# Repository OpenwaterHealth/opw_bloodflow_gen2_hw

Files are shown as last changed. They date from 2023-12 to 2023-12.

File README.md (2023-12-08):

# opw_bloodflow_gen2_hw
Openwater Blood Flow Gen 2 Hardware

system

Openwater Gen 2 Blood Flow System hardware designs are detailed in this repository. 

## Table of Contents

- [Getting Started](#getting-started)
  - [Prerequisites](#prerequisites)
- [Usage](#usage)
- [Contributing](#contributing)
- [License](#license)

## Getting Started

Before getting started with the design data included in this repo, you may want to visit the Gen 2 Blood Flow Hardware Wiki for some background information on the system and its design. You may also want to review the See the [Openwater Blood Flow Gen 2 Software](link) and [Openwater Blood Flow Gen 2 Analysis](link) repos for additional information about the system and its operation. 

### Prerequisites

Required software will depend on the type of data desired by the user. In general, we have tried to include generic formats, viewable with free tools, wherever possible. Data in proprietary formats such as SolidWorks and Altium native are provided for the convenience of users with access to those tools.  

Several file types commonly used include
- STEP assembly files and SolidWorks native files for mechanical assemblies
- PDFs of assembly and component drawings, electrical schematics, datasheets, and documentation
- Gerber files for printed circuit designs
- Altium design files for circuit designs and layouts
- DXF and STL files for individual mechanical components

### Repository Contents
[Mechanical design files](mechanical), which include
- [Major subsystems](mechanical/major_subsystems)
- Additional design files for various components and subassemblies in various formats ([PDF](mechanical/pdf), [STL](mechanical/stl), [DXF](mechanical/dxf))

[Electrical design files](electrical), which includes printed circuit board assemblies and harnessing

[System design](system_design) files which include high-level documents describing the design of the blood flow system

[Assembly and Test](assembly_and_test) which includes various documents detailing contruction of various device subsystems

## Contributing

We welcome contributions from the community. If you have ideas for improvements or find any issues, please open an issue or submit a pull request.

Before contributing, please read our [Contributing Guidelines](CONTRIBUTING.md).

## License
opw_bloodflow_gen2_hw is licensed under the GNU Affero General Public License v3.0. See [LICENSE](LICENSE) for details.

## Investigational Use Only
CAUTION - Investigational device. Limited by Federal (or United States) law to investigational use. opw_bloodflow_gen2_hw has *not* been evaluated by the FDA and is not designed for the treatment or diagnosis of any disease. It is provided AS-IS, with no warranties. User assumes all liability and responsibility for identifying and mitigating risks associated with using this software.

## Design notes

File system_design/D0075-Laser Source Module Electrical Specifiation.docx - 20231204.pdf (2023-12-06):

Subsystem Specification | Doc #: | D0075
Laser Source Module Electrical Specification | Rev: | 01
| Page: | Page 1 of 10

### 1. PURPOSE

The purpose of this document is to provide specifications and relevant technical details for the laser source electrical subsystem.

### 2. SCOPE

This document provides an overview of the complete Gen 2 measurement system, Laser source module subsystem functional blocks and signal interconnect, critical component information, diode laser driver requirements and signaling, Tapered amplifier driver requirements and signaling laser safety and support components.

### 3. GOVERNING SAFETY STANDARDS AND COMPONENT REFERENCES

Document No. Document Title

All references to specific policies, procedures, or work instructions in this document are to the latest revision of that document unless otherwise noted. All references to personnel in this document are to that person or his/her designated representative unless otherwise stated.

### 4. DEFINITIONS AND ACRONYMS

### 4.1. Acronyms used in this Document

ASSY – Assembly
BOM – Bill of Materials
DWG – Drawing
FAB – Fabrication
OTS – Off the Shelf
PCA – Printed Circuit Assembly
PCB – Printed Circuit Board

### 5. GENERATION 2 LASER MEASUREMENT SYSTEM

5.1. System Overview – Measurement system is divided into seven sybsystems:
- Laser Source Module
- RVP-‐TDA4Vx Instrument Controller
- Isolation Interface Module
- Patient-‐Applied-‐Part
- Power Distribution/Regulator Module
- Trigger/Timing Module
- Laser Distribution and Control

Figure 5.1 illustrates the overall system architecture with relevant signals and interconnects shown, color coded by function.

Subsystem Specification | Doc #:

Laser Source Module Electrical Specification
Page: | Page 2 of 10

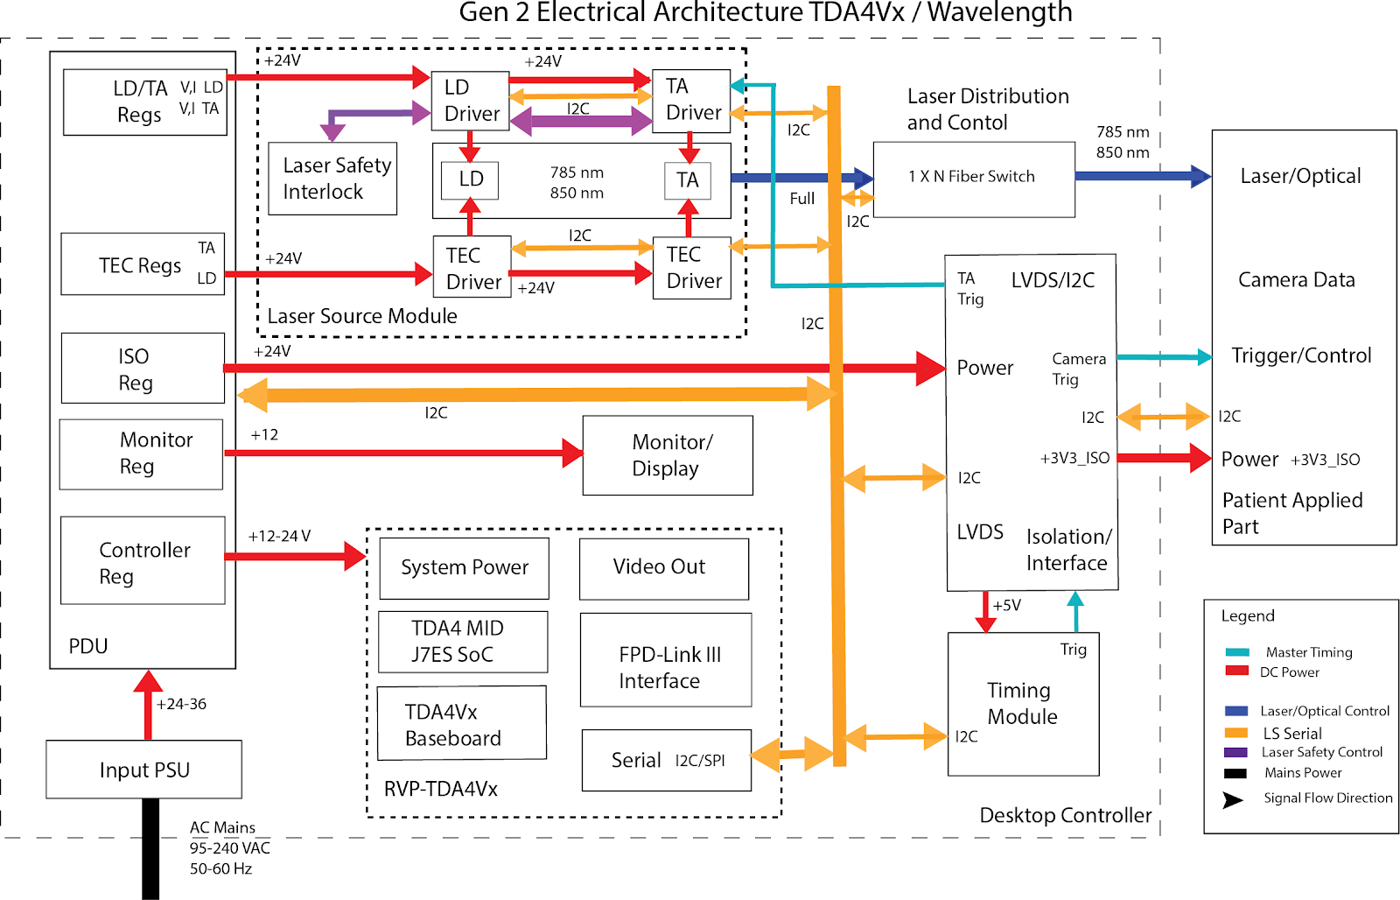
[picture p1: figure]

Figure 5.1 System Architecture

Laser Source Module-‐ Optical system used to deliver optical energy to patient. Contains two OTS semiconductor laser devices, detailed in the critical components section of this document.

RVP-‐TDA4Vx Instrument Controller-‐ Computational platform used for system control, signal and data processing and patient applied part interface.

Isolation/Interface Module-‐ | Patient-‐applied-‐part power, interface and control
Patient-‐Applied-‐Part-‐ | Device containing multiple camera sensors, control electronics, laser
distribution optics and data pathway electronics

Power Distribution/Regulator Module-‐Instrument subsystem power distribution, monitoring and control

Trigger/Timing Module-‐Instrument system master timing module. Provides timing and synchronization signals to laser source, patient applied part and instrument controller

Laser Source Module Electrical Specification
Page: | Page 3 of 10
Laser Distribution and Control-‐ | Commercial, serially controlled 1 x 8 Fiber optic switch
5.2. Laser Source Module Subsystem Detail – Diode Laser and Tapered Amplifier devices are both driven by low noise, voltage controlled current sources. Input power to these devices is supplied by discrete, individually regulated supplies from the power distribution unit. In addition to device drivers, this subsystem also provides TEC drivers for each semiconductor laser to ensure that the device operates at a constant, well defined temperature. Figure 5.2 illustrates the device driver arrangement and relationship to the power distribution unit.

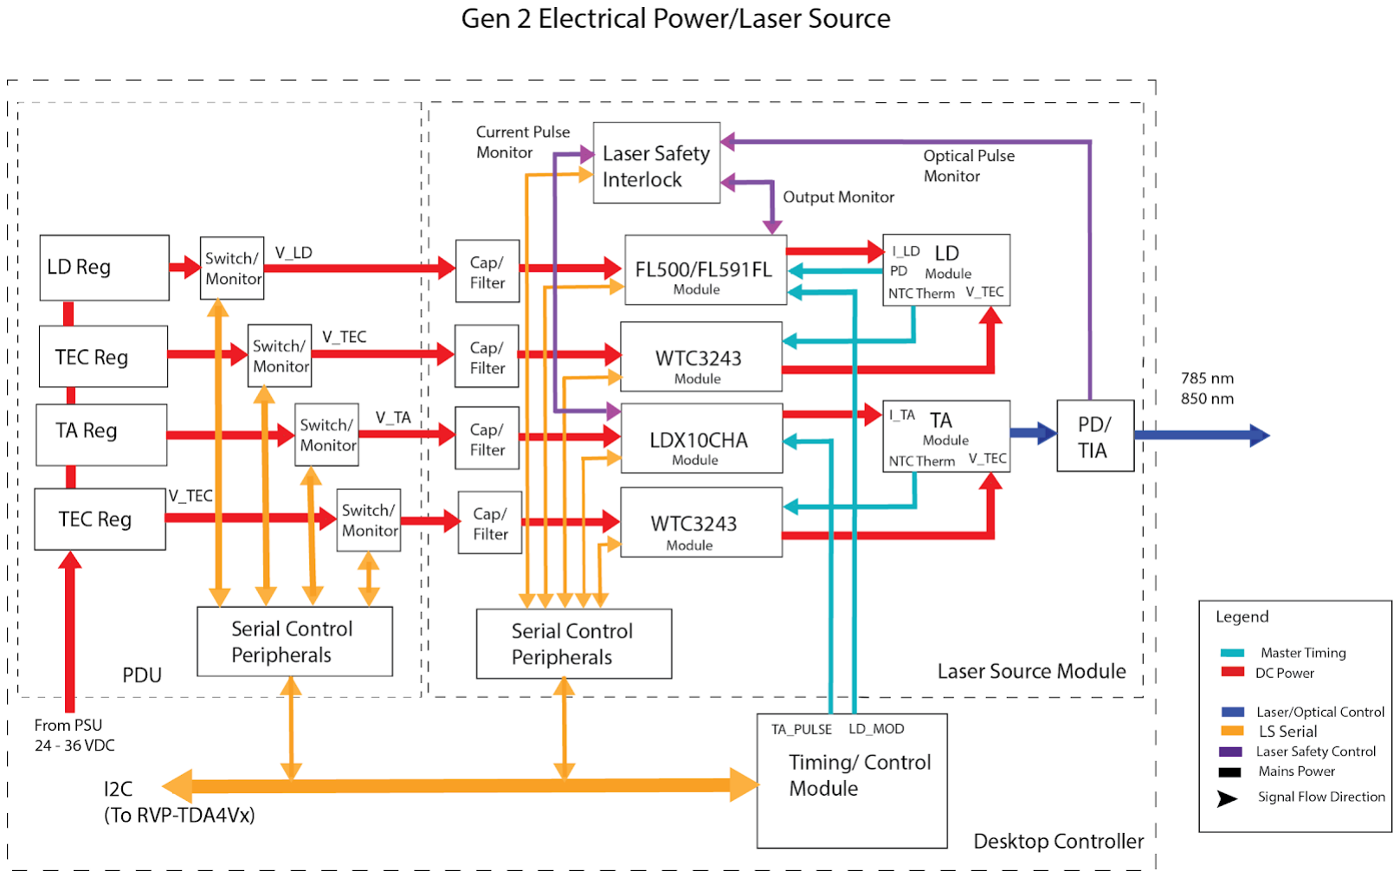
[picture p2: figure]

Figure 5.2 Laser Driver Subsystem

Architecture provides a switched, monitored low noise power supply to each of the driver modules shown in this system. Also included in this is a set of monitor and control peripherals, connected to one of the I2C networks in the system serial control backbone. Also illustrated in this diagram is the trigger/timing signals supplied to each device. Section 5.3 describes the laser diode driver in detail, and section 5.4 describes the tapered amplifier system in detail.

Laser Source Module Electrical Specification
Page: | Page 4 of 10
5.3. Laser Diode Driver – Laser diode module is a commercially sourced, single frequency diode laser module in a dual, inline butterfly type package. Figure 5.3 illustrates the device and critical specifications.

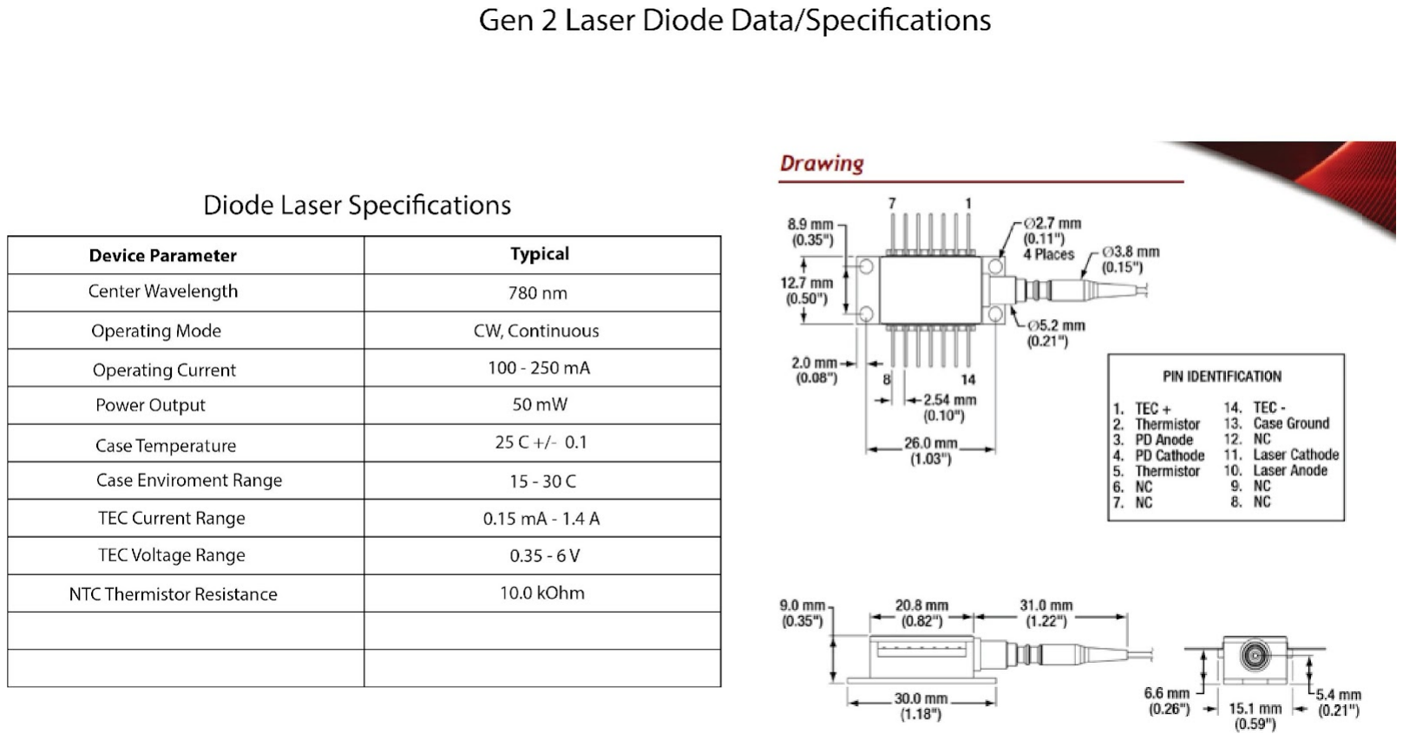
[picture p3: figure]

Figure 5.3 Laser Diode Specification

Items to note: Device is operated CW, fiber coupled, and has an integrated TEC, and NTC thermistor for temperature control. Active device is isolated from the case and the current intention is to attach the case to a defined ground potential, consistent with safety and EMC testing requirements. Temperature regulation is 25 C +/-‐ 0.1.

The diode laser driver contains a constant current driver, control and monitor electronics and is implemented using a set of commercial OTS components from Wavelength Electronics. Figure 5.4 illustrates the driver architecture and relevant Wavelength components. Note that the driver should provide support for a small signal modulation input, in addition to the CW current level. Back facet device monitor is not used in driver operation, but is used in conjunction with the Laser Safety Interlock.

Laser Source Module Electrical Specification
Page: | Page 5 of 10

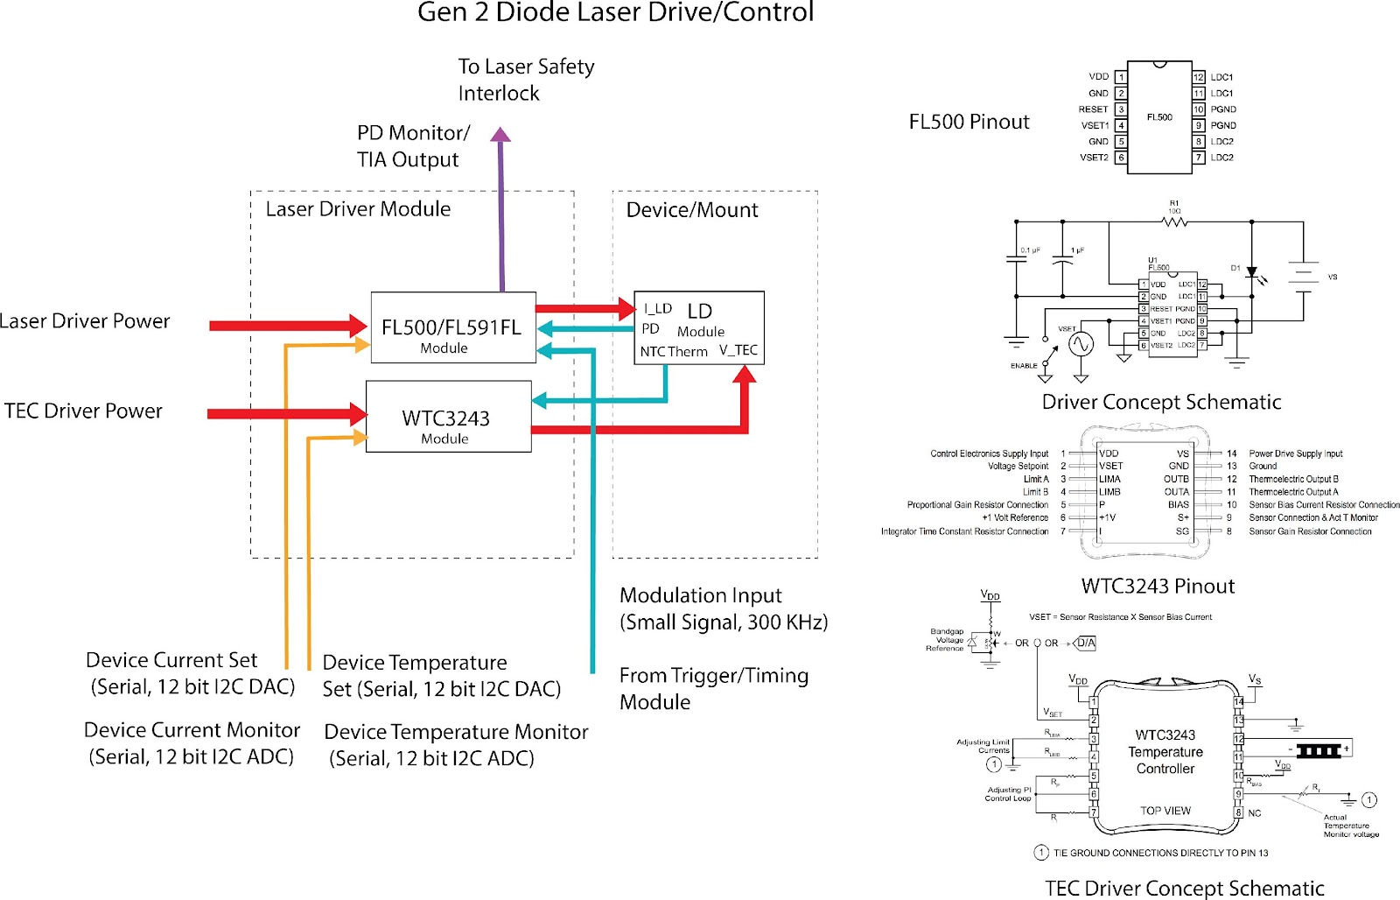
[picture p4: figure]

Figure 5.4 Laser Driver Module Details

Laser Source Module Electrical Specification
Page: | Page 6 of 10
5.4. Tapered Amplifier Driver-‐ | Tapered Amplifier module is a commercially sourced, narrow bandwidth
semiconductor laser module in a dual, inline butterfly type package. Figure 5.5 illustrates the device and critical specifications. Items to note: Device is operated QCW mode, fiber coupled, and has an integrated TEC, and NTC thermistor for temperature control. Active device is isolated from the case and the current intention is to attach the case to a defined ground potential, consistent with safety and EMC testing requirements. Temperature regulation is 25 C +/-‐ 0.1.

The Tapered Amplifier driver control and monitor electronics and is implemented using a set of commercial OTS components from Wavelength Electronics. Figure 5.6 illustrates the driver architecture and relevant Wavelength components. Note that the driver should provide support for CW operation at a lower current level than specified in the QCW peak specification

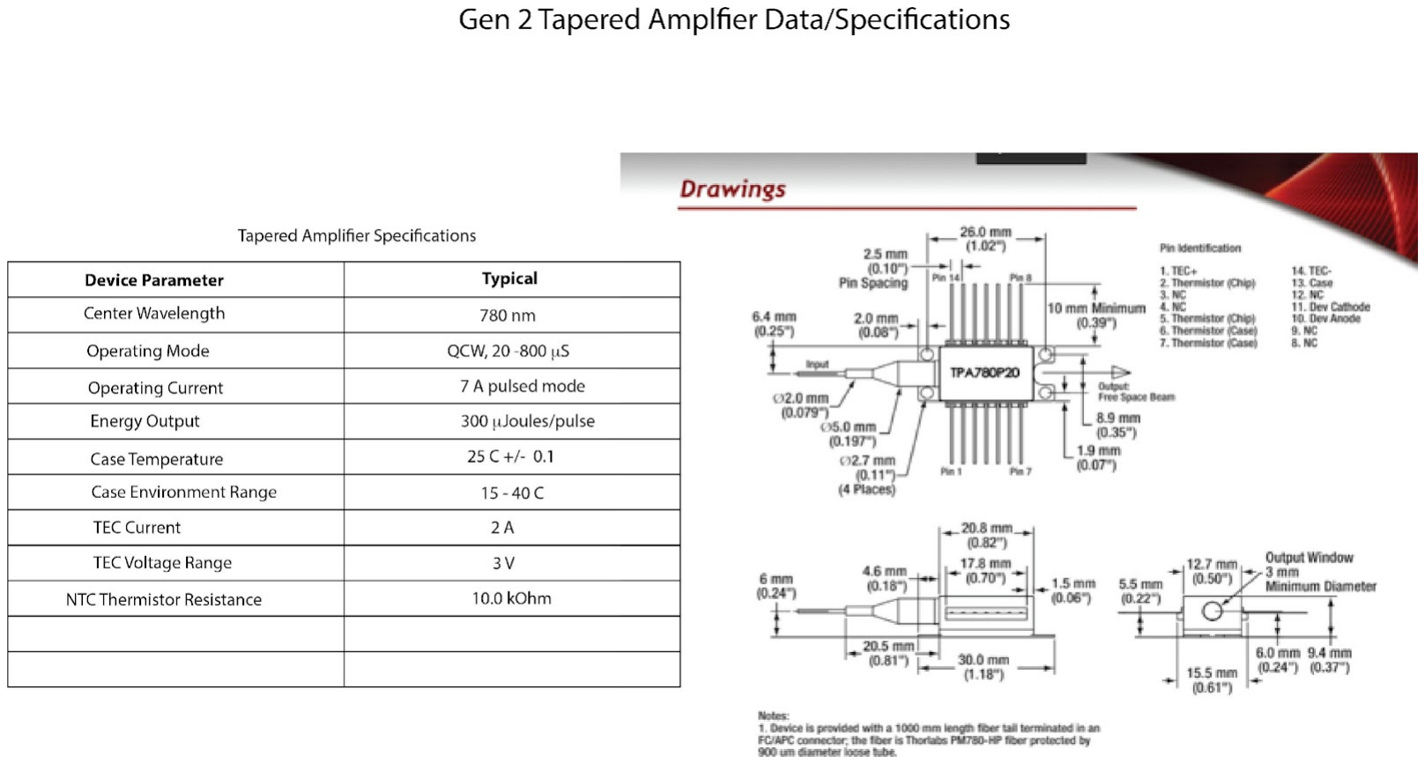
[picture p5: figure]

Laser Source Module Electrical Specification
Page: | Page 7 of 10

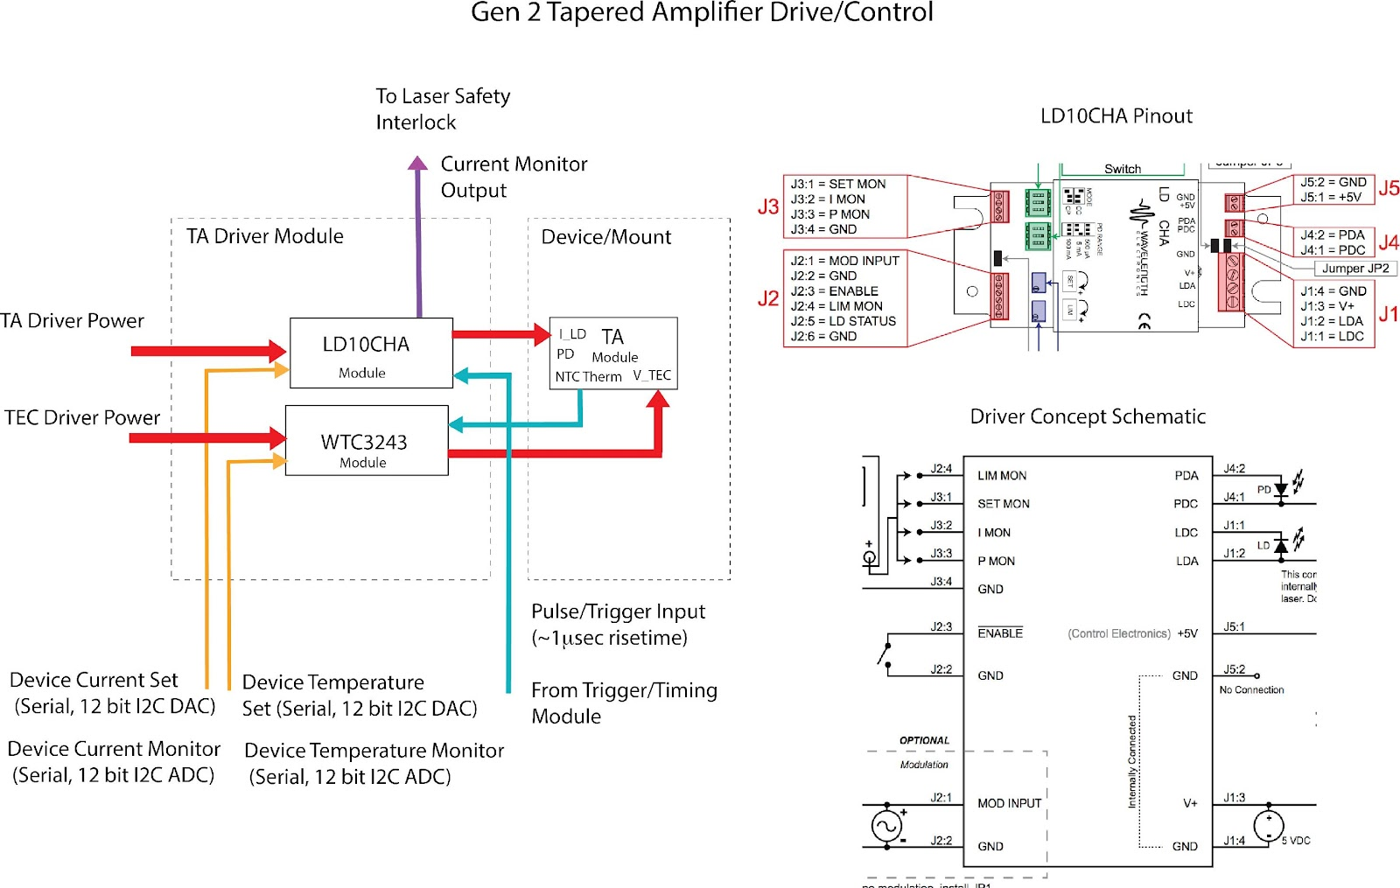
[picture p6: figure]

Figure 5.6 Tapered Amplifier Details

5.5. Laser Safety Interlock – Laser source operation uses an interlock circuit that monitors the laser for proper operation. Circuit monitors both single pulse energy and multiple pulse energy. Both electrical
and optical monitors are employed for measurements and serve to provide redundant monitoring, consistent with IEC 60825.

In addition to laser output monitoring, the interlock system also provides protection against device failure. An essential part of the monitoring system checks for Diode Laser input and proper operation of the device. Operating the Tapered Amplifier without a Diode Laser (Seed) input will lead to irreversible damage to the Tapered Amplifier. Figure 5.7 illustrates the logical schematic of the Laser Safety Interlock with some technical details.

Laser Source Module Electrical Specification
Page: | Page 8 of 10

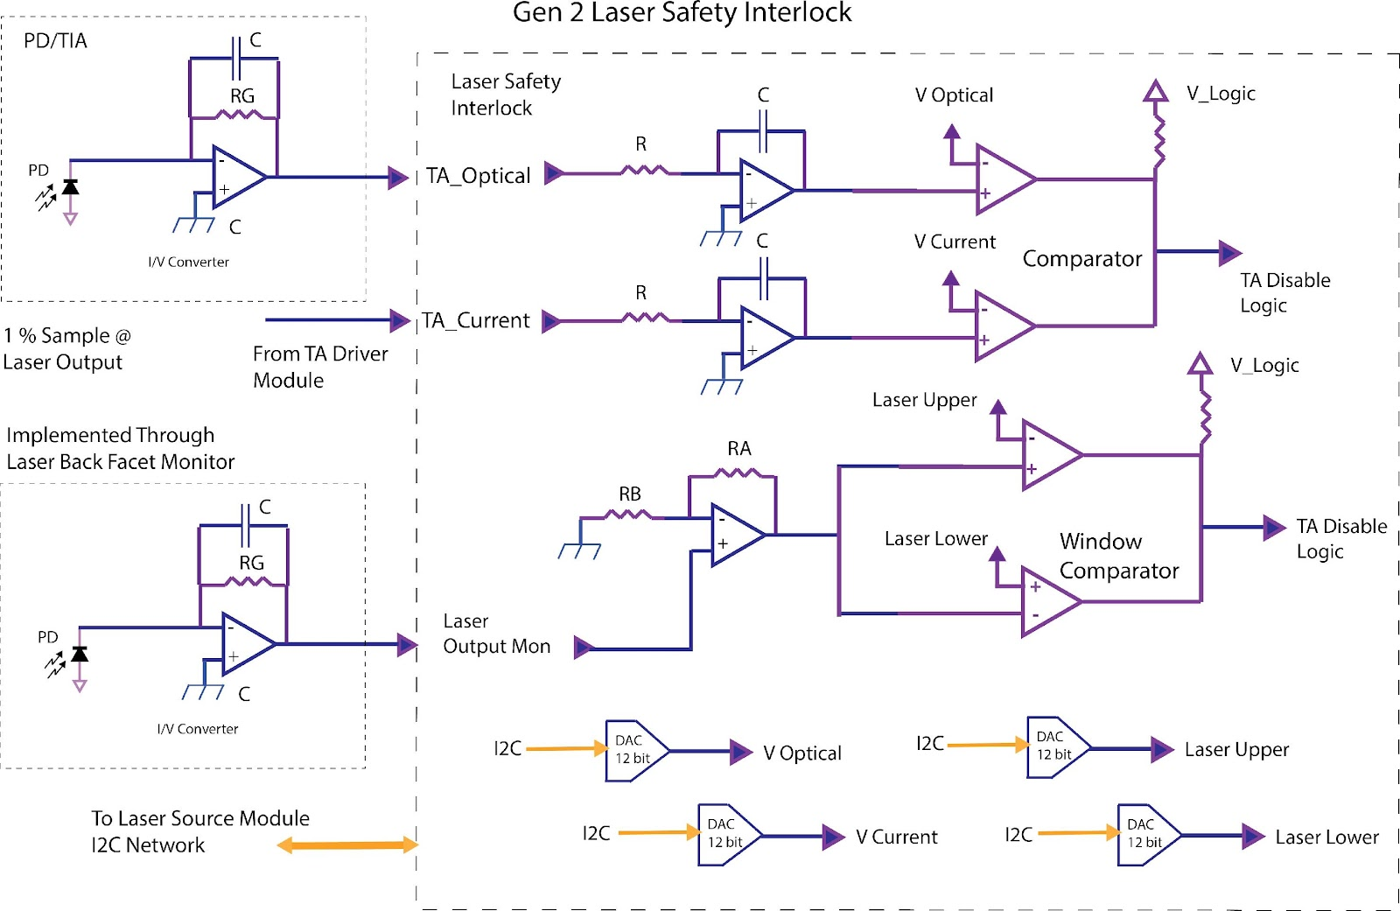
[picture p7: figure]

Figure 5.7 Tapered Amplifier Details

### 6. MECHANICAL CONSIDERATIONS

6.1. General Comments-‐ Each active device is mounted on a thermally conductive heat sink. Device electrical connections are made through a ZIF type socket attached to a PCA adjacent to the device.
The PCA system also provides connections to the respective drivers through a short multiconductor cable. Interconnect is set up to minimize crosstalk between systems. Laser and Tapered Amplifier components are degraded by electrical noise from power supply elements and the TEC drivers.
Module design should be consistent with best practices in low noise electronic system design. Figure 6.1 illustrates the general concept of device mounting and a proposed ZIF socket from Azimuth.

Laser Source Module Electrical Specification
Page: | Page 9 of 10

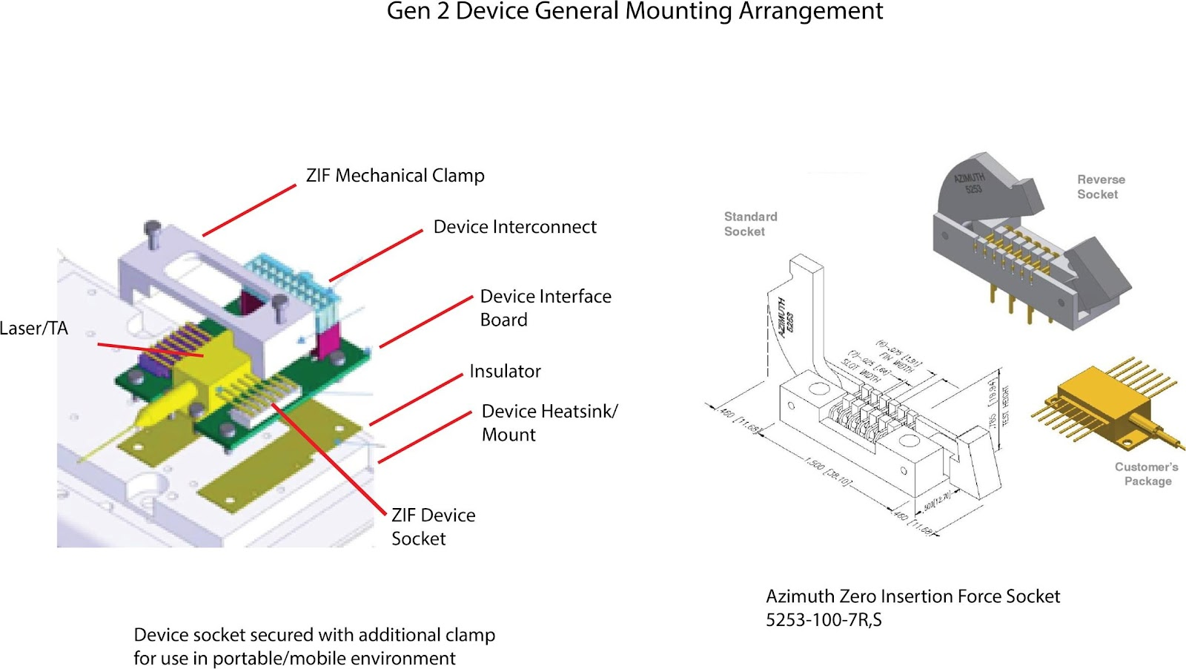
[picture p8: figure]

Figure 6.1 Device Electrical Socket and Mechanical Arrangement

In order to preserve flexibility, all pins should be carried from the device and board to the driver, to permit use of packaged devices that may have an alternative pinout.

6.2. PCA Considerations-‐ | Physical architecture is based on two PCAs per device:
- Device PCA-‐ | provides electrical interconnect to the active device, and provide electrical
interconnect to the device driver module, as described in this specification. PCA should also provide mounting holes for attachment to heat sink/thermal system
- Driver PCA-‐ Active device driver, TEC module, support and monitor electronics and
interconnect to PDU. PCA should also include mounting holes for attachment to the rest of the system .
Where possible, OTS or otherwise commercial components are acceptable and should be used in lieu of custom designed parts

### 6.3. PCA Mechanical Outlines-‐

6.4. Units:
6.4.1. Dimensions and Tolerances shall be specified in metric units of measure unless otherwise

Laser Source Module Electrical Specification
Page: | Page 10 of 10

specified.
6.4.2. Tolerances should be specified for x, 0.x, and 0.xx.

### 6.5. Drawing Notes

6.6. Critical dimensions (if needed):

### 6.7. Part Labeling

6.7.1. PCB
6.7.2. PCA

### 7. TBD

- Part number and revision level on silkscreen layer as board size permits.
- PCA part number, revision level and serial
number in human readable text and barcode
(QR preferred) on permanent tamper-‐proof label as board size permits or directive to see
labeling instruction with appropriate document
number.
- Part number and revision level on ESD packaging. (May be specified on part in Agile)

### 8. QUALITY RECORDS

### 9. APPENDIX

End of Document

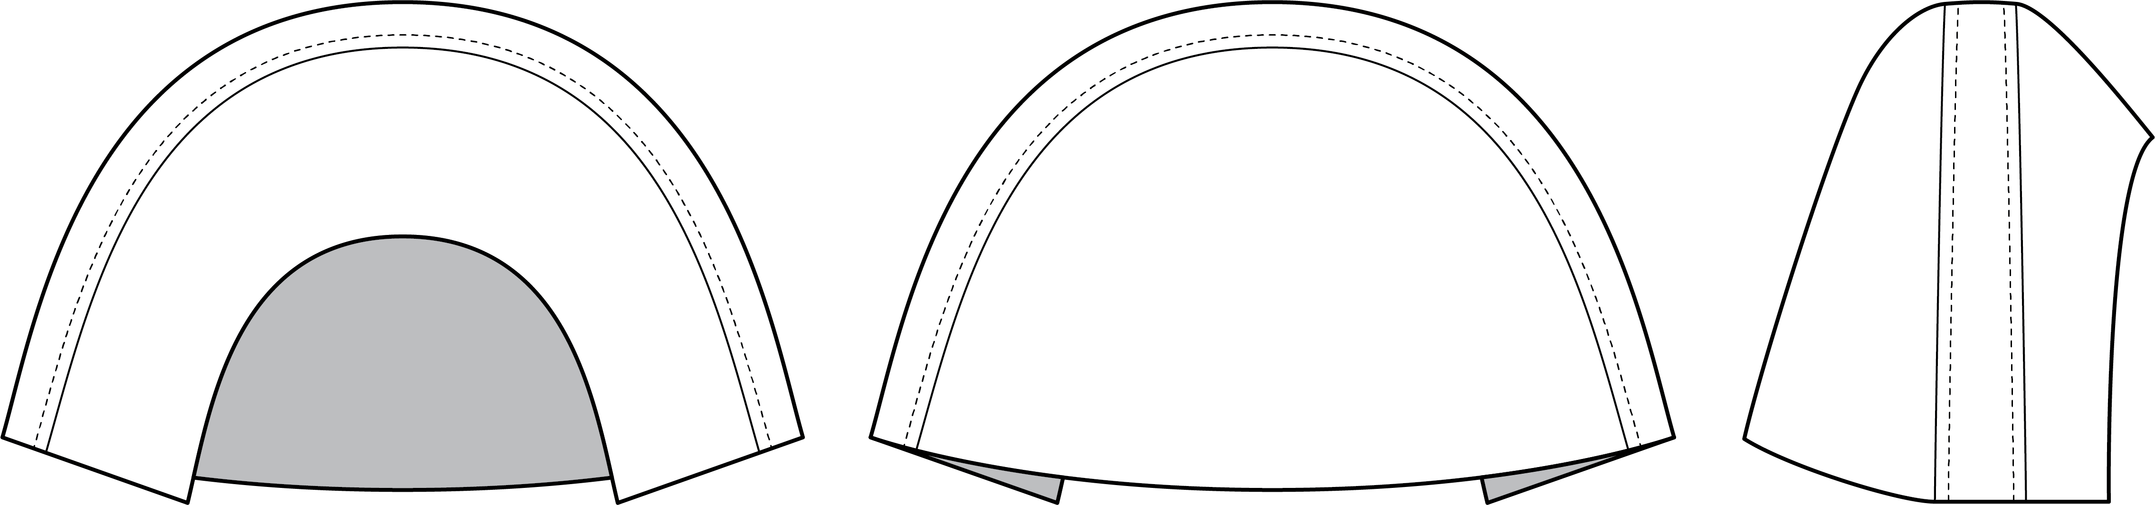
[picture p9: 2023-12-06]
mechanical/major_subs/accessories/OPEN WATER_FLAT_HEADSEAT DRAPE.png

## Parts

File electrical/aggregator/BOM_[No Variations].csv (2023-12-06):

Name | Description | Designator | Part Number | Price | Qty
GRT188R6YA475KE13D | Multi-Layer Ceramic Capacitor 4.7uF 35V X5R ±10% 0603 Paper T/R | C200, C201, C202, C211, C212, C213, C214, C300, C301, C302, C311, C312, C313, C314 | Murata GRT188R6YA475KE13D, | 2.996 | 14
GRM188R6YA106MA73D | Chip Multilayer Ceramic Capacitors for General Purpose, 0603, 10uF, X5R, 15%, 20%, 35V | C203, C207, C219, C303, C307, C319 | Murata GRM188R6YA106MA73D, | 1.26 | 6
C0805C474K3RACTU | CAP CER 0.47UF 25V X7R 0805 | C204, C215, C304, C315, C502, C503, C506, C507, C510, C511, C514, C515, C518, C519, C522, C523, C526, C527, C530, C5531 | Yageo CC0805KKX7R8BB474, | 0.4 | 20
C0603C223K5RACTU | Ceramic Capacitor 0.022Uf 50V, X7R, 10%, 0603, Full Reel | C205, C216, C305, C316 | KEMET C0603C223K5RACTU, |  | 4
C1608C0G1E103J080AA | Multilayer Ceramic Capacitors 10nF ±5% 25V C0G SMD 0603 | C206, C217, C218, C223, C306, C317, C318, C323, C500, C504, C508, C512, C516, C520, C524, C528 | TDK C1608C0G1E103J080AA, | 0.928 | 16
06035C333KAT2A | General Purpose Ceramic Capacitor, 0603, 33nF, 10%, X7R, 15%, 50V | C224, C324 | Kyocera AVX 06035C333KAT2A, | 0.0184 | 2
C0603X104K5RACTU | CAP CER 0.1UF 50V X7R 0603 | C400, C401, C501, C505, C509, C513, C517, C521, C525, C529 | KEMET C0603X104K5RACTU, | 0.26 | 10
SM02B-SURS-TF (L |  | J100, J101, J102, J103, J104, J105, J106, J107 |  |  | 8
SM04B-SURS-TF(LF |  | J110, J111, J112, J113, J114, J115, J116, J117 |  |  | 8
CONN JST SM06B-SRSS-TB | CONN HEADER SMD R/A 6POS 1MM | J120 |  |  | 1
CRCW04024K70FKED | RES Thick Film, 4.7kΩ, 1%, 0.063W, 100ppm/°C, 0402 | R100, R101, R400, R401, R402, R403, R404, R405, R406, R407, R408, R409, R410, R411, R412, R413, R414, R415, R416, R420 | Vishay Dale CRCW04024K70FKED, |  | 20
CRCW0603620RFKEA |  | R200, R211, R300, R311 | Vishay CRCW0603620RFKEA, | 0.012 | 4
ERJ-3EKF4993V |  | R201, R301 | Panasonic ERJ-3EKF4993V, | 0.01 | 2
RT0603FRE07280KL | RES SMD 280K OHM 1% 1/10W 0603 | R206, R217, R306, R317 | Yageo RT0603FRE07280KL, | 0.32 | 4
RT0603BRD0761K9L | RES SMD 61.9K OHM 0.1% 1/10W | R207, R218, R307, R318 | Yageo RT0603BRD0761K9L, | 0.7344 | 4
KTR03EZPF1002 | Res Thick Film 0603 10kΩ 1% 0.1W ±100ppm/°C Automotive Paper T/R | R219, R319 | Rohm KTR03EZPF1002, | 0.3 | 2
KTR03EZPF6801 | Res Thick Film 0603 6.8kΩ 1% 0.1W ±100ppm/°C Automotive Paper T/R | R224, R324 | Rohm KTR03EZPF6801, | 0.32 | 2
CRCW06031K00FKEA | RES Thick Film, 1kΩ, 1%, 0.1W, 100ppm/°C, 0603 | R225, R226, R325, R326 | Vishay Dale CRCW06031K00FKEA, | 0.17 | 4
RL0603FR-070R5L |  | R500, R501, R502, R503, R504, R505, R506, R507 | Yageo RL0603FR-070R5L, | 0.392 | 8
LT3066IMSE#PBF | Adjustable LDO current limit | U200, U211, U300, U311 |  |  | 4
LT1637CS8#TRPBF | Single Channel, High Voltage, Micropower Rail-to-Rail Operational Amplifier, 1 MHz Typical GBW, 0.35 V/us Typical SR, 1.8 to 44 V, 8-Pin SOIC (S8-8), Commercial, Pb-Free, Reel | U223, U323 | Analog Devices / Linear Technology LT1637CS8#TRPBF, | 10.28 | 2
PCA9548ADGVR | 8-Channel I2C Switch with Reset, 2.3 to 5.5 V, -40 to 85 degC, 24-pin TVSOP (DGV), Green (RoHS & no Sb/Br) | U400 | Texas Instruments PCA9548ADGVR | 1.65 | 1
PCA9538PW_Q900,118 | Integrated Circuit | U401 |  |  | 1

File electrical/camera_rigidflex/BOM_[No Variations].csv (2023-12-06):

Name | Description | Designator | Part Number | Price | Qty
0402YD105KAT2A | 'CAP CER 1UF 16V 10% X7R 0402 | C10, C11, C14, C15, C16, C17, C18, C22, C24, C25, C31, C33, C35, C315 | Kyocera AVX 0402YD105KAT2A, | 0.602 | 14
C1608X5R1A106M080AC | Multilayer Ceramic Capacitors 10μF ±20% 10V X5R SMD 0603 | C20, C27, C37, C210, C312, C329 | TDK C1608X5R1A106M080AC, | 2.06 | 6
0402YD104KAT2A | CAP CER 0.1UF 16V X5R 0402 | C21, C23, C26, C28, C38, C310, C313, C317 | Kyocera AVX 0402YD104KAT2A, | 0.22 | 8
CAP CER 0.1UF 16V X5R 0402 | CAP CER 0.1UF 16V X5R 0402 | C29 | Taiyo Yuden EMK105BJ104MV-F | 0.1 | 1
GRM155R71C103KA01D | Chip Capacitor, 10 nF, 16 V, 10%, -55 to 125 degC, 0402 (1005 Metric), RoHS, Tape and Reel | C32, C34, C36, C39, C311, C314 | Murata GRM155R71C103KA01D, | 0.15 | 6
CL03A104KO3NNNC | Cap Ceramic 100nF 16V X5R ±10% Pad SMD 0201 +85°C T/R | C40, C42, C45, C53, C57 | Samsung CL03A104KO3NNNC, | 0.25 | 5
CAP CER 0.1UF 6.3V X5R 0201 | CAP CER 0.1UF 6.3V X5R 0201 | C49 | Samsung CL03A104KQ3NNNH | 0.1 | 1
0201ZD105MAT2A | CAP CER 1UF 10V X5R 0201 | C54 | Kyocera AVX 0201ZD105MAT2A | 0.10567 | 1
GRM155R70J223KA01D | Chip Multilayer Ceramic Capacitors for General Purpose, 0402, 22000pF, X7R, 15%, 10%, 6.3V | C316 | Murata GRM155R70J223KA01D | 0.07279 | 1
C1005X7R1H333K050BB | Multilayer Ceramic Capacitors 33nF ±10% 50V X7R SMD 0402 | C318, C319 | TDK C1005X7R1H333K050BB, |  | 2
SDM03U40-7 | DIODE SCHOTTKY 30V 30MA SOD523 | D40 | Diodes SDM03U40-7 | 0.0246 | 1
APHHS1005SURCK | LED RED CLEAR CHIP SMD | DS43 | Kingbright APHHS1005SURCK | 0.35 | 1
SML-P11MTT86 | LED YELLOW/GREEN CLEAR 1006 SMD | DS44 | Rohm SML-P11MTT86 | 0.335 | 1
SM02B-SURS-TF (L |  | J10 |  |  | 1
128-0711-201 | Connector | J11 |  |  | 1
SM04B-SURS-TF(LF |  | J12 |  |  | 1
BLM15AX102SN1D | Chip Ferrite Bead, 0402, 1000Ω @ 100MHz, 0.49Ω, 25%, 350mA | L30, L33, L35 | Murata BLM15AX102SN1D, | 0.3 | 3
CRCW040240K2FKED | RES, 20 k, 1%, 0.063 W, 0402 | R17 |  |  | 1
ERJ-1GEF4701C |  | R20, R21, R24, R25, R45, R56, R57 | Panasonic ERJ-1GEF4701C, |  | 7
RES SMD 0 OHM JUMPER 1/20W 0201 | 0 Ohms Jumper 0.05W, 1/20W Chip Resistor 0201 (0603 Metric) Thick Film | R22, R23, R27, R28 |  |  | 4
CRCW040210K0JNED | RES, 10k ohm, 5%, 0.063W, 0402 | R30, R31, R34 |  |  | 3
CRCW04021K50JNED | RES, 1.5 k, 5%, 0.063 W, 0402 | R32, R323 |  |  | 2
CRCW040240K2FKED | RES, 40.2 k, 1%, 0.063 W, 0402 | R36 |  |  | 1
ERJ-1GN0R00C |  | R37, R52, R53, R55 | Bourns CR0201-J/-000GLF, | 0.06 | 4
ERJ-2RKF49R9X |  | R38 | Panasonic ERJ-2RKF49R9X | 0.006 | 1
CRCW0201100KFKED |  | R40 | Vishay Dale CRCW0201100KFKED | 0.22 | 1
CRCW020110K0FKED |  | R41 | Vishay Dale CRCW020110K0FKED | 0.022 | 1
ERJ-2GEJ301X |  | R43, R44 | Panasonic ERJ-2GEJ301X, | 0.004 | 2
ERJ1GNF2003C |  | R58 | Panasonic ERJ-1GNF2003C | 0.092 | 1
LP5907SNX-2.8/NOPB | None | U10 | Texas Instruments LP5907SNX-2.8/NOPB | 0.166 | 1
LP5907SNX-1.9/NOPB, LP5907SNX-1.2/NOPB | None | U11, U12 | Texas Instruments LP5907SNX-1.8/NOPB, | 1.2248 | 2
DS90UB953TRHBRQ1 | 2MP MIPI CSI-2 FPD-Link III Serializer for 2MP/60fps Cameras and RADAR, RHB0032P (VQFN-32) | U30 |  |  | 1
SN74LVC2G00YZPR | IC GATE NAND 2CH 2-INP 8DSBGA | U40 |  |  | 1
SN74AUC2G06YZPR | IC INVERTER 2CH 2-INP 6DSBGA | U42 |  |  | 1
SN74AUP1G07YFPR | Low-Power Single Buffer/Driver with Open-Drain Outputs, YFP0004AAAA, LARGE T&R | U45 | Texas Instruments SN74AUP1G07YFPR | 0.3127 | 1
PCA9306YZTR | Dual Bi-Directional I2C-Bus and SMBus Voltage Level-Translator, 0 to 5.5 V, -40 to 85 degC, 8-pin DSBGA (YZT), Green (RoHS & no Sb/Br) | U50 | Texas Instruments PCA9306YZTR | 0.77 | 1

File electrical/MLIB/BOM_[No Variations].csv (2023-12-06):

Line # | Name | Description | Designator | Revision Status | Quantity | Footprint | Manufacturer 1 | Manufacturer Part Number 1 | Manufacturer Lifecycle 1 | Supplier 1 | Supplier Part Number 1 | Supplier Subtotal 1
 | RES_0603_10kΩ, DNL | Res Thick Film 0603 10K Ohm 1% 0.1W(1/10W) ±100ppm/C Molded SMD Automotive T/R | R309, R310, R311, R312, R326, R327, R341, R346, R347, R349, R350, R351, R352, R353, R360, R400, R401, R402, R403, R404, R421, R422, R423, R424, R425, R426, R427, R428, R430, R431, R432, R433, R434, R435, R436, R437, R450, R451, R452, R454, R455, R457, R458, R504, R505, R506, R507, R508, R509, R511, R512, R514, R515, R518, R520, R521, R522, R523, R524, R526, R527, R530, R531, R532, R533, R534, R536, R537, R540, R541, R542, R544, R545, R546, R547, R550, R551, R552, R553, R554, R555, R556, R557, R558, R561, R562, R563, R564, R565, R566, R567, R568, R569, R570, R571, R572, R573, R574, R575, R576, R577, R578, R579, R580, R581, R582, R583, R584, R585, R586, R595, R802, R815, R816, R817, R818, R819, R820, R825, R826, R827, R4453 | Up to date | 122 | FP-RMCF0603-MFG | SEI | RMCF0603FT10K0 | Volume Production | Mouser | 708-RMCF0603FT10K0 | 0.854
 | UMK325AB7106KM-T | CAP CER 10UF 50V X7R 1210 | C100, C105, C113 | Up to date | 3 | FP-MK325A-MFG | Taiyo Yuden | UMK325AB7106KM-T | Volume Production | Digi-Key | 587-3167-1-ND | 2.16
 | CC0805KKX5R9BB105 | 0805 1 uF 50 V ±10% Tolerance X5R SMT Multilayer Ceramic Capacitor | C101, C106, C114, C871, C872 | Up to date | 5 | FP-CC0805-0_85-MFG | Yageo | CC0805KKX5R9BB105 | Volume Production | Farnell | 4166941 | 1.02516
 | CAP_4uF7_0805_50V | Multilayer Ceramic Capacitor 4.7uF 10% 50V 0805 T/R | C107, C115, C119, C121, C130, C226 | Up to date | 6 | CAPC2013X135X45NL10T25 | TDK | C2012X7R1H475K125AE | Volume Production | Farnell | 3416186 | 2.5259
 | GCM1885C1H272JA16D | Ceramic Capacitor for Automotive 2.7nF ±5% 50VDC C0G 0603 Paper T/R | C110 | Up to date | 1 | FP-GCM188-0_1-MFG | Murata | GCM1885C1H272JA16D | Volume Production | Newark | 92AH4798 | 0.5
 | CAP_0603_20pF_50V | Ceramic Capacitor, Multilayer, Ceramic, 50V, 5% +Tol, 5% -Tol, C0G, 30ppm/Cel TC, 0.00002uF, Surface Mount, 0603 | C117, C133 | Up to date | 2 | CAPC0603(1608)100_L | Walsin Technologies | 0603N200J500CT | Volume Production | Digi-Key | 1292-1498-1-ND | 0.2
 | CAP_0603_100nF_50V | Ceramic Capacitor, Multilayer, Ceramic, 50V, 10% +Tol, 10% -Tol, X5R, 15% TC, 0.1uF, Surface Mount, 0603 | C181, C182, C227, C230 | Up to date | 4 | FP-RMCF0603-IPC_B | Kyocera AVX | 06035D104KAT2A | Volume Production | Newark | 95W9226 | 0.11
 | Capacitor 10µF +/-20% 25V 0805 | Chip Capacitor, 10µF +/-20%, 25V, 0805, Thickness 1.45 mm | C207 | Up to date | 1 | CAPC0805(2012)145_L | TDK | C2012X5R1E106K125AB | Volume Production | Arrow Electronics | C2012X5R1E106K125AB | 0.2843
 | CAP_0603_10nF_25V | Ceramic Capacitor, Multilayer, Ceramic, 25V, 10% +Tol, 10% -Tol, X7R, -/+15ppm/Cel TC, 0.01uF, 0603 | C215, C228 | Up to date | 2 | FP-RMCF0603-IPC_B | Multicomp | MC0603B103K250CT | Volume Production | Farnell | 1759022 | 0.24264
 | KCM55WR7YA476MH01L | CAP CER 47UF 35V X7R SMD | C216, C217, C218 | Up to date | 3 | FP-KCM55W-6_1_5_3_6_7_1_2-MFG | Murata | KCM55WR7YA476MH01L | Volume Production | Farnell | 2990711 | 9.89976
 | C0603X104K5RACTU | CAP CER 0.1UF 50V X7R 0603 | C300, C301, C302, C305, C307, C308, C311, C315, C316, C326, C327, C329, C351, C352, C401, C403, C476, C504, C509, C510, C540, C543, C550, C560, C572, C580, C600, C603, C604, C605, C608, C611, C612, C615, C618, C622, C625, C631, C634, C636, C638, C641, C651, C701, C703, C704, C705, C709, C711, C712, C715, C4521 | Up to date | 52 | FP-C0603-CJ-MFG | KEMET | C0603X104K5RACTU | Volume Production | Newark | 94M5632 | 1.352
 | UMK107AB7105KA-T | Ceramic Capacitor General Use 1uF ±10% 50V X7R 0603 | C81, C304, C325, C340, C350, C380, C400, C404, C475, C505, C508, C520, C524, C534, C541, C551, C561, C573, C601, C602, C606, C607, C610, C613, C614, C621, C624, C630, C633, C637, C640, C650, C700, C702 | Up to date | 34 | FP-0603-L_1_6_0_15-W_0_8-IPC_C | Taiyo Yuden | UMK107AB7105KA-T | Volume Production | Mouser | 963-UMK107AB7105KA-T | 4.284
 | 06033C474KAT2A | General Purpose Ceramic Capacitor, 0603, 470nF, 10%, X7R, 15%, 25V | C516, C548 | Up to date | 2 | FP-0603-L_1_6_0_15-W_0_81-MFG | Yageo | CC0603KRX5R8BB474 | Volume Production | Mouser | 603-CC603KRX5R8BB474 | 0.26
 | BAT54T1G | Schottky Barrier Diode, 2-Pin SOD-123, Pb-Free, Tape and Reel | D508, D509, D510, D512, D513, D514, D524, D525, D534, D535, D540, D541, D542, D545, D546, D547 | Up to date | 16 | ONSC-SOD-123-2-425-04_V | ON Semiconductor | BAT54T1G | Volume Production | Mouser | 863-BAT54T1G | 3.136
 | 39-28-9088 | Connector | J200 |  | 1 | 39-28-9088
 | 39-30-2040 | CONN HEADER VERT 4POS 4.2MM | J201, J202, J207 | Up to date | 3 | FP-39-30-2040-MFG | Molex | 39-30-2040 | Volume Production | Newark | 58J8596 | 0.969
 | 39-28-9168 | Connector | J203, J204 |  | 2 | 39-28-9168
 | 46999-0621 | Conn Power HDR 2 POS 4.2mm Solder ST Thru-Hole 2 Terminal 1 Port | J205 | Up to date | 1 | Molex_46999-0621_2pin_4mm2Pitch | Molex | 46999-0621 | Volume Production | Digi-Key | 0469990621-ND | 0.92
 | 39-28-9188 | Connector | J210 |  | 1 | 39-28-9188
 | 22-23-2031 | WIRE-BOARD CONNECTOR HEADER 3 POSITION, 2.54MM; Product Range:KK 6373 Series; Contact Termination Type:Through Hole; Gender:Header; No. of Contacts:3; Pitch Spacing:2.54mm; Contact Plating:Tin Plated Contacts; Contact Material:Brass ;RoHS Compliant: Yes | J800 | Up to date | 1 | MOLX-22-23-2031_V | Molex | 22-23-2031 | Volume Production | Mouser | 538-22-23-2031 | 0.27
 | RT0603BRE074K7L, DNL | RES SMD 4.7K OHM 0.1% 1/10W 0603 | R113, R215, R216, R250, R251, R252, R253, R254, R255, R256, R257, R259, R260, R261, R262, R263, R264, R265, R266, R275, R276, R277, R278, R279, R280, R281, R282, R705, R706, R707, R708, R709, R710, R711, R712, R713, R714, R715, R716, R750, R751, R800, R801, R803, R804, R805, R806, R807, R808, R809, R810, R811, R812, R814, R851, R852, R853, R854, R856, R857, R858, R898, R899, R8855 | Up to date | 64 | FP-RT0603-MFG | Yageo | RT0603BRE074K7L | Volume Production | Newark | 69AK5029 | 6.592
 | CRCW0603499KFKEA | RES Thick Film, 499kΩ, 1%, 0.1W, 100ppm/°C, 0603 | R117 | Up to date | 1 | FP-CRCW0603-e3-IPC_B | Vishay | CRCW0603499KFKEA | Volume Production | Newark | 27W4274 | 0.03
 | CRCW06031M20FKEA | RES Thick Film, 1.2MΩ, 1%, 0.1W, 100ppm/°C, 0603 | R119, R134 | Up to date | 2 | FP-CRCW0603-e3-IPC_A | Vishay | CRCW06031M20FKEA | Volume Production | Newark | 27W4071 | 0.19
 | CRCW06031K05FKEA | RES Thick Film, 1.05kΩ, 1%, 0.1W, 100ppm/°C, 0603 | R125 | Up to date | 1 | FP-CRCW0603-e3-MFG | Vishay | CRCW06031K05FKEA | Volume Production | Newark | 52K8020 | 0.005
 | CRCW0603121RFKEA | RES Thick Film, 121Ω, 1%, 0.1W, 100ppm/°C, 0603 | R126 | Up to date | 1 | FP-CRCW0603-e3-IPC_A | Vishay | CRCW0603121RFKEA | Volume Production | Newark | 52K8116 | 0.003
 | CRCW06032K20FKEAHP | RES Thick Film, 2.2kΩ, 1%, 0.33W, 100ppm/°C, 0603 | R301, R307, R315 | Up to date | 3 | FP-CRCW0603-HPe3-IPC_A | Vishay | CRCW06032K20FKEAHP | Volume Production | Newark | 65AC3387 | 0.066
 | RC0603JR-070RL, DNL | Chip Resistor, 0 Ohm, +/- 5%, 0.1 W, -55 to 155 degC, 0603 (1608 Metric), RoHS, Tape and Reel | R328, R329, R332, R333, R334, R335, R336, R337, R358, R481, R482, R861, R862, R863, R864, R865, R866, R867, R868, R869, R870, R871, R872, R873, R874, R875, R876, R877, R878, R879, R880 | Up to date | 31 | RESC1608X55X25ML10T15 | Yageo | RC0603JR-070RL | Volume Production | Mouser | 603-RC0603JR-070RL | 0.279
 | CRCW06030000Z0EAHP | RES Thick Film, 0Ω, , 0.33W, , 0603 | R342, R405 | Up to date | 2 | FP-CRCW0603-HPe3-MFG | Vishay Dale | CRCW06030000Z0EAHP | Volume Production | Digi-Key | 541-0.0SBCT-ND | 0.28
 | CRCW0603300RFKEA | RES Thick Film, 300Ω, 1%, 0.1W, 100ppm/°C, 0603 | R510, R516, R543, R548 | Up to date | 4 | FP-CRCW0603-e3-IPC_A | Vishay | CRCW0603300RFKEA | Volume Production | Mouser | 71-CRCW0603-300-E3 | 0.17
 | MCR03ERTF2493 | Thick Film Chip Resistor, 0603, 249kΩ, 1%, 100ppm/°C, 0.1W, 50V | R517, R525, R535, R549 | Up to date | 4 | FP-MCR03-IPC_C | Rohm | MCR03ERTF2493 | Volume Production
 | 5003 | Test Point, Orange, Height 4.6 mm, Tail Length 3 mm, 1-Pin THD, RoHS | TP325, TP326, TP330, TP331, TP350, TP351, TP353, TP403, TP404, TP405, TP500, TP501 | Up to date | 12 | KSTN-5003 | Keystone Electronics | 5003 | Volume Production | Farnell | 2301280 | 3.24654
 | R-78E15-0.5 | Power Supply | U100 |  | 1 | R78E1205
 | LTC1144IS8#PBF | Switched-Capacitor Wide Input Range Voltage Converter with Shutdown, 8-pin SOIC (S8-8), -40 to 85 degC, Pb-Free | U102, U123 | Up to date | 2 | LT-S8-8_L | Analog Devices / Linear Technology | LTC1144IS8#PBF | Volume Production | Arrow Electronics | LTC1144IS8#PBF | 9.8672
 | R-78E5.0-1.0 | Power Supply | U105 |  | 1 | R78E5010
 | LM1085ISX-ADJ/NOPB | 3A Low Dropout Positive Regulators, 3-pin TO-263, Pb-Free | U107 | Up to date | 1 | KTT0003B_M | TI National Semiconductor | LM1085ISX-ADJ/NOPB | Volume Production | Mouser | 926-LM1085ISXADJNOPB | 1.99
 | R-78E9.0 0.5 | Power Supply | U112 |  | 1 | R78E5010
 | LT3085EMS8E#TRPBF | LDO Regulator Pos 0V to 36V 0.5A 8-Pin MSOP EP T/R | U117, U130 | Up to date | 2 | LT-MS8E-8-1880X1680TP_M | Analog Devices / Linear Technology | LT3085EMS8E#TRPBF | Volume Production | Arrow Electronics | LT3085EMS8E#TRPBF | 11.13
 | LT3094EMSE#PBF | Integrated Circuit | U119 |  | 1 | SOP65P490X110-13N
 | TCR2LF33,LM(CT | IC REG LINEAR 3.3V 200MA SMV | U180 | Up to date | 1 | FP-SSOP5-P-0_95-MFG | Toshiba | TCR2LF33,LM(CT | Volume Production | Arrow Electronics | TCR2LF33,LM(CT | 0.27
 | P82B96TD,118 | IC REDRIVER I2C 1CH 400KHZ 8SO | U250, U254, U258, U262 | Up to date | 4 | FP-SOT96-1-MFG | NXP Semiconductors | P82B96TD,118 | Volume Production | Mouser | 771-P82B96TD-T | 17.36
 | MCP4716A1T-E/CH | 10-Bit Voltage Output Digital-to-Analog Converter with EEPROM and I2C Interface, 6-Pin SOT-23, Extended Temperature, Tape and Reel | U300 | Up to date | 1 | SOT-23-CH6_N | Microchip | MCP4716A1T-E/CH | Volume Production | Arrow Electronics | MCP4716A1T-E/CH | 1.0258
 | LTC6088CGN#PBF | Quad Channel, Rail-to-Rail, CMOS Operational Amplifier, 14 MHz Typical GBW, 7.2 V/us Typical SR, 2.7 to 5.5 V, 16-Pin SOP (GN-16), Commercial, Pb-Free | U302, U508, U520, U540 | Up to date | 4 | LT-GN-16_M | Analog Devices / Linear Technology | LTC6088CGN#PBF | Volume Production | Digi-Key | LTC6088CGN#PBF-ND | 18.4
 | MCP3021A5T-E/OT | Low Power 10-Bit A/D Converter With I2C Interface, 5-Pin SOT-23, Extended Temperature, Tape and Reel | U310, U312 | Up to date | 2 | SOT-23-OT5_M | Microchip | MCP3021A5T-E/OT | Volume Production | Arrow Electronics | MCP3021A5T-E/OT | 2.6464
 | SN74LVC1G07DBVR | Single Buffer/Driver With Open-Drain Output, DBV0005A, LARGE T&R | U311 | Up to date | 1 | DBV0005A_M | Texas Instruments | SN74LVC1G07DBVR | Volume Production | Arrow Electronics | SN74LVC1G07DBVR | 0.3693
 | MCP47CMB22-E_UN | Integrated Circuit | U325 |  | 1 | SOP50P490X110-10N
 | AD633ARZ-R7 | Low Cost Analog Multiplier, 20 V/us, 6 mA, -40 to 85 degC, 8-Pin SOIC (R), RoHS, Tape and Reel | U330, U480 | Up to date | 2 | ADI-R-8_L | Analog Devices | AD633ARZ-R7 | Volume Production | Newark | 47AK1335 | 20.74
 | LM4050BIM3-2.5/NOPB | Precision Micropower Shunt Voltage Reference, 3-pin SOT-23, Pb-Free | U340, U404 | Up to date | 2 | MF03A_M | TI National Semiconductor | LM4050BIM3-2.5/NOPB | Volume Production | Arrow Electronics | LM4050BIM3-2.5/NOPB | 3.5914
 | OPA703NA/250 | CMOS, Rail-to-Rail I/O, Operational Amplifier, 4 to 12 V, -40 to 85 degC, 5-pin SOT23 (DBV5), Green (RoHS & no Sb/Br) | U350, U400 | Up to date | 2 | DBV0005A_M | Texas Instruments | OPA703NA/250 | Volume Production | Arrow Electronics | OPA703NA/250 | 6.284
 | SN74LVC1G04DCKR | Single Inverter, DCK0005A, LARGE T&R | U354, U403 | Up to date | 2 | DCK0005A_N | Texas Instruments | SN74LVC1G04DCKR | Volume Production | Newark | 29AH7591 | 0.11
 | MCP47FEB28-20E/ST | D/A Converter, 1 Func, Serial Input Loading, 7.8us Settling Time, PDSO20 | U406, U414 | Up to date | 2 | TSOP65P640X120-20N_20-TSSOP | Microchip | MCP47FVB18T-20E/ST | Unknown | Digi-Key | 150-MCP47FVB18T-20E/STCT-ND | 14.82
 | LTC6087CMS8#PBF | Dual Channel, Rail-to-Rail, CMOS Operational Amplifier, 14 MHz Typical GBW, 7.2 V/us Typical SR, 2.7 to 5.5 V, 8-Pin SOP (MS8-8), Commercial, Pb-Free | U504, U550, U560, U572, U580 | Up to date | 5 | LT-MS8-8_N | Analog Devices / Linear Technology | LTC6087CMS8#PBF | Volume Production | Digi-Key | LTC6087CMS8#PBF-ND | 15.25
 | LMV7219M5 | 7 nsec, 2.7V to 5V Comparator with Rail-to- Rail Output, 5-pin SOT-23 | U600, U602, U605, U606, U610, U612, U614, U616, U620, U624, U630, U633, U637, U640 | Up to date | 14 | DBV0005A_L | TI National Semiconductor | LMV7219M5 | Volume Production | Arrow Electronics | LMV7219M5 | 46.97
 | SN74LVC2G08DCTR | Dual 2-Input Positive-AND Gate, DCT0008A, LARGE T&R | U604, U618, U636, U700, U702 | Up to date | 5 | DCT0008A_M | Texas Instruments | SN74LVC2G08DCTR | Volume Production | Arrow Electronics | SN74LVC2G08DCTR | 2.9085
 | SN74LVC2G74DCTR | Single Positive-Edge-Triggered D-Type Flip-Flop with Clear and Preset, DCT0008A, LARGE T&R | U704, U708, U711, U714 | Up to date | 4 | DCT0008A_M | Texas Instruments | SN74LVC2G74DCTR | Volume Production | Arrow Electronics | SN74LVC2G74DCTR | 2.7944
 | SN74LVC1G08DCKR | Single 2-Input Positive-AND Gate, DCK0005A, LARGE T&R | U716, U717, U718 | Up to date | 3 | DCK0005A_M | Texas Instruments | SN74LVC1G08DCKR | Volume Production | Newark | 32AK8974 | 1.179
 | SN74LVC1G27DBVR | IC GATE NOR 1CH 3-INP SOT23-6 | U719 | Up to date | 1 | FP-DBV0006A-IPC_B | Texas Instruments | SN74LVC1G27DBVR | Volume Production | Arrow Electronics | SN74LVC1G27DBVR | 0.4136
 | PCA9544APWR | 4-Channel I2C and SMBus Multiplexer with Interrupt Logic, 2.3 to 5.5 V, -40 to 85 degC, 0-pin TSSOP (PW), Green (RoHS & no Sb/Br) | U800 | Up to date | 1 | PW0020A_M | Texas Instruments | PCA9544APWR | Volume Production | Mouser | 595-PCA9544APWR | 2.29
 | PCAL6416APW,118 | IC I/O EXPANDER 16BIT 24TSSOP | U825 | Up to date | 1 | FP-SOT355-1-MFG | NXP Semiconductors | PCAL6416APW,118 | Volume Production | Arrow Electronics | PCAL6416APW,118 | 1716.25
 | ADS7828EB/2K5 | 12-Bit 50 kSPS ADC I2C Low Power 8-Channel Multiplexer Internal 2.5 V Reference, -40 to 85 degC, 16-pin SOP (PW16), Green (RoHS & no Sb/Br) | U850, U855 | Up to date | 2 | TI-PW16_L | Texas Instruments | ADS7828EB/2K5 | Volume Production | Arrow Electronics | ADS7828EB/2K5 | 9.71
 | CRCW060324K9FKEA | RES Thick Film, 24.9kΩ, 1%, 0.1W, 100ppm/°C, 0603 | R304, R305 | Up to date | 2 | FP-CRCW0603-e3-IPC_B | Vishay | CRCW060324K9FKEA | Volume Production | Newark | 52K8316 | 0.006
 | CRCW060312K4FKEA | RES Thick Film, 12.4kΩ, 1%, 0.1W, 100ppm/°C, 0603 | R306 | Up to date | 1 | FP-CRCW0603-e3-IPC_B | Vishay | CRCW0603-12K4FKEA | Volume Production
 | TCJB106M025R0150E | 10uF 25V ±20% 150mΩ 1210 SMD Polymer Capacitor | C102, C103, C104, C123, C124, C125, C860, C867, C869 | Up to date | 9 | FP-TCJB-MFG | Kyocera AVX | TCJB106M025R0150E | Volume Production | Mouser | 581-CJB106M025R0150E | 4.71
 | LTST-C190GKT | LED GREEN CLEAR CHIP SMD | D721, D722, D723, D724, D860 | Up to date | 5 | FP-LTST-C190GKT-MFG | Vishay Lite-On | LTST-C190GKT | Volume Production | Future Electronics | 3106685 | 0.965
 | 171971-0008 | Connector | J215 |  | 1 | SHDR8W90P0X254_1X8_2278X510X1216P
 | SN74LVC07APWR | IC BUF NON-INVERT 5.5V 14TSSOP | U275 | Up to date | 1 | FP-PW0014A-MFG | Texas Instruments | SN74LVC07APWR | Volume Production | Arrow Electronics | SN74LVC07APWR | 0.389
 | SN74LVC2G07DBVR | Dual Buffer/Driver with Open-Drain Output, DBV0006A, LARGE T&R | U280 | Up to date | 1 | DBV0006A_M | Texas Instruments | SN74LVC2G07DBVR | Volume Production | Arrow Electronics | SN74LVC2G07DBVR | 0.4134
 | PCA9540BD,118 | IC INTERFACE SPECIALIZED 8SO | U830 | Up to date | 1 | FP-SOT96-1-MFG | NXP Semiconductors | PCA9540BD,118 | Unknown | Newark | 61AC1254 | 1.46
 | MAX3221EAE+ | IC TXRX RS232 120KBPS SD 16-SSOP | U860 | Up to date | 1 | FP-A16-2-MFG | Maxim | MAX3221EAE+ | Not Recommended for New Design | Farnell | 2519449 | 6.10243
 | SC18IM704PWJ | Integrated Circuit | U866, U868 |  | 2 | SOP65P640X110-16N
 | PCA9508DP,118 | Integrated Circuit | U870 |  | 1 | SOP65P490X110-8N
 | C0603C104K5RAC7411 | CAP CER 0.1UF 50V X7R 0603 | C250, C254, C258, C262, C310, C312, C330, C332, C406, C414, C421, C422, C423, C424, C425, C426, C427, C428, C430, C431, C432, C433, C434, C435, C436, C437, C480, C482, C708, C714, C716, C717, C718, C719, C861, C862, C863, C864, C865, C866, C868, C870, C873 | Up to date | 43 | FP-C0603C-CF-MFG | KEMET | C0603C104K5RAC7411 | Volume Production | Mouser | 80-C0603C104K5R7411 | 1.763
 | CRCW0603499RFKEA | RES Thick Film, 499Ω, 1%, 0.1W, 100ppm/°C, 0603 | R752, R753, R754, R755, R860 | Up to date | 5 | FP-CRCW0603-e3-MFG | Vishay | CRCW0603499RFKEA | Volume Production | Newark | 61M5398 | 0.19
 | C0603C105K3PACTU | CAP CER 1UF 25V X5R 0603 | C108, C116, C118, C120, C122, C131, C132, C180, C183, C251, C255, C259, C263, C275, C280, C331, C333, C407, C415, C481, C483, C800, C825, C830, C850, C855 | Up to date | 26 | FP-C0603C105K3PACTU-MFG | KEMET | C0603C105K3PACTU | Volume Production | Newark | 25M8783 | 1.56
 | 901-144-8RFX | Coaxial Connector, 18 GHz, 50 Ohm, -65 to 165 degC, 5-Pin THD, RoHS, Bulk | J380, J450 | Up to date | 2 | AMPH-901-144-8RFX_V | Amphenol RF | 901-144-8RFX | Volume Production
 | CR0603-FX-2002ELF | Thick Film Chip Resistors 0603 20kΩ 0.1W 1% 100ppm/°C | R41, R607, R608, R613, R615, R617, R619, R620, R622, R623, R624, R627, R631, R632, R634, R635, R638, R639, R642, R649 | Up to date | 20 | FP-CR0603-IPC_C | Bourns | CR0603-FX-2002ELF | Volume Production | Newark | 33AK8347 | 0.06
 | RC0603FR-0710KL | RES 10K OHM 1% 1/10W 0603 | R475, R476, R477, R478 | Up to date | 4 | FP-RC0603-0_55-IPC_C | Yageo | RC0603FR-0710KL | Volume Production | Mouser | 603-RC0603FR-0710KL | 0.11
 | KTR03EZPF5103 | Res Thick Film 0603 510kΩ 1% 0.1W ±100ppm/°C Automotive Paper T/R | R609, R612, R614, R618, R621, R625, R630, R633, R637, R640 | Up to date | 10 | FP-KTR03-MFG | Rohm | KTR03EZPF5103 | Volume Production | Mouser | 755-KTR03EZPF5103 | 0.7
 | SN74LV1T34DBVR | IC BUF NON-INVERT 5.5V SOT23-5 | U380 | Up to date | 1 | FP-DBV0005A-IPC_B | Texas Instruments | SN74LV1T34DBVR | Volume Production | Arrow Electronics | SN74LV1T34DBVR | 0.3213
 | LT1783CS5#TRPBF | Single Channel, Micropower, Over-The-Top, Operational Amplifier, RRIO, 1.25 MHz Typical GBW, 0.42 V/us Typical SR, 2.2 to 18 V, 5-Pin SOT23 (S5-5), Commercial, Pb-Free, Reel | U475 | Up to date | 1 | LT-S5-5-TSOT-23_M | Analog Devices / Linear Technology | LT1783CS5#TRPBF | Volume Production

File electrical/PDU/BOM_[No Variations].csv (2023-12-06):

Line # | Name | Description | Designator | Quantity | Manufacturer 1 | Manufacturer Part Number 1 | Manufacturer Lifecycle 1 | Supplier 1 | Supplier Part Number 1 | Supplier Unit Price 1 | Supplier Subtotal 1
 | 470uF 35V | CAP ALUM 470UF 20% 35V RADIAL | C1, C1a, C1b, C2, C2a, C2b, C11, C26, C65, C94, C140 | 11 | Rubycon | 35ZLH470MEFC10X16 | Volume Production | Digi-Key | 1189-1890-ND | 0.436 | 4.796
 | DNP | CAPACITOR NOT POPULATED 0603 | C1a, C1b | 2
 | 10uF 50V | CAP CER 10UF 50V X5R 1206 | C3, C4, C12, C21, C24, C27, C39, C41, C42, C44, C63, C66, C71, C74, C82, C85, C92, C95, C99, C117, C135, C138, C141, C159, C180, C181 | 26 | Murata | GRT31CR61H106ME01L | Volume Production | Digi-Key | 490-12457-1-ND | 0.255 | 6.63
 | 0.1uF 50V | CAP CER 0.1UF 50V X7R 0603 | C5, C6, C7, C8, C9, C10, C13, C14, C15, C16, C18, C19, C22, C25, C28, C29, C34, C35, C40, C43, C45, C48, C49, C50, C51, C52, C53, C54, C55, C56, C57, C58, C59, C60, C61, C62, C64, C67, C68, C70, C75, C76, C77, C79, C81, C86, C87, C88, C91, C93, C96, C97, C100, C102, C105, C107, C111, C112, C114, C115, C118, C120, C123, C125, C129, C130, C132, C133, C136, C139, C142, C143, C148, C153, C154, C155, C157, C160, C162, C163, C168, C173, C174, C175, C176, C177, C178, C179, C182 | 89 | KEMET | C0603C104K5RACTU | Volume Production | Digi-Key | 399-C0603C104K5RAC7867DKR-ND | 0.0329 | 3.29
 | 680pF 50V | CAP CER 680PF 50V X7R 0603 | C17, C90, C113, C131, C156 | 5 | Vishay Vitramon | VJ0603Y681KXACW1BC | Volume Production | Digi-Key | 720-VJ0603Y681KXACW1BCCT-ND | 0.1 | 0.5
 | 100uF 50V | CAP ALUM 100UF 20% 50V RADIAL | C20, C72, C73, C83, C84, C98, C116, C134, C158 | 9 | Rubycon | 50ZLH100MEFC8X11.5 | Volume Production | Digi-Key | 1189-2327-ND | 0.27 | 2.7
 | 10000pF 50V | CAP CER 10000PF 50V X7R 0603 | C23, C69, C80, C101, C119, C137, C161 | 7 | KEMET | C0603C103K5RACTU | Volume Production | Digi-Key | 399-C0603C103K5RAC7867CT-ND | 0.061 | 0.61
 | 47uF 25V | CAP CER 47UF 25V X5R 1206 | C30, C31, C32, C33, C144, C145, C146, C147, C149, C164, C165, C166, C167, C169 | 14 | TDK | C3216X5R1E476M160AC | Volume Production | Digi-Key | 445-8047-1-ND | 0.734 | 10.276
 | 15000pF 50V | CAP CER 0.015UF 50V X7R 0603 | C36, C108, C126, C150, C170 | 5 | KEMET | C0603C153K5RACTU | Volume Production | Digi-Key | 399-C0603C153K5RAC7867CT-ND | 0.1 | 0.5
 | 47pF 50V | CAP CER 47PF 50V C0G/NP0 0603 | C37, C46, C47, C109, C127, C151, C171 | 7 | Samsung | CL10C470JB8NNNC | Volume Production | Digi-Key | 1276-1037-1-ND | 0.039 | 0.39
 | 68pF 50V | CAP CER 68PF 50V C0G/NP0 0603 | C38, C110, C128, C152, C172 | 5 | Samsung | CL10C680JB8NNNC | Volume Production | Digi-Key | 1276-1135-1-ND | 0.037 | 0.37
 | 0.47uF 50V | CAP CER 0.47UF 50V X7R 0603 | C78, C89 | 2 | TDK | C1608X7R1H474K080AC | Volume Production | Digi-Key | 445-5952-1-ND | 0.23 | 0.46
 | 100uF 10V | CAP CER 100UF 10V X5R 1206 | C103, C104, C106, C121, C122, C124 | 6 | TDK | C3216X5R1A107M160AC | Volume Production | Digi-Key | 445-6007-1-ND | 1.03 | 6.18
 | TVS 24V | TVS DIODE 24VWM 38.9VC DO214AC | D1, D16, D18 | 3 | Littelfuse | SMAJ24CA | Volume Production | Newark | 71J1995 | 0.429 | 1.287
 | Green Vf 2.0 | LED GREEN 0603 SMD | D2, D6, D10, D14, D17, D19, D22, D25, D29, D32 | 10 | Vishay Lite-On | LTST-C191KGKT | Volume Production | Digi-Key | 160-1446-1-ND | 0.136 | 1.36
 | 60V 7A | DIODE SCHOTTKY 60V 7A POWERDI5 | D3, D4, D15, D20, D21, D24, D27, D28, D31 | 9 | Diodes | PDS760-13 | Volume Production | Digi-Key | PDS760DICT-ND | 0.788 | 7.88
 | TVS 12V | TVS DIODE 12VWM 19.9VC DO214AC | D5, D30, D33 | 3 | Littelfuse | SMAJ12CA | Volume Production | Digi-Key | SMAJ12CALFCT-ND | 0.43 | 1.29
 | B240A-E3/5AT | DIODE SCHOTTKY 40V 2A DO214AC | D7, D9, D11, D13 | 4 | Vishay Semiconductors | B240A-E3/61T | Volume Production | Digi-Key | B240A-E3/61TGICT-ND | 0.4 | 1.6
 | TVS 5V | TVS DIODE 5VWM 9.2VC DO214AC | D8, D23, D26 | 3 | Littelfuse | SMAJ5.0CA | Volume Production | Digi-Key | SMAJ5.0CALFCT-ND | 0.43 | 1.29
 | TVS 3.3V | TVS DIODE 3.3VWM 14.1VC 0402 | D12 | 1 | Comchip | CPDQ3V3-HF | Volume Production | Digi-Key | 641-1476-1-ND | 0.32 | 0.32
 | 10A 125VAC SMD | FUSE BRD MNT 10A 125VAC/VDC SMD | FUS1 | 1 | Littelfuse | 0154010.DR | Volume Production | Digi-Key | F1251CT-ND | 3.16 | 3.16
 | 10142708-02200LF | CONN HEADER VERT 2POS 5.7MM | J200 | 1 | Amphenol ICC / FCI | 10142708-02200LF | Unknown | Mouser | 649-10142708-02200LF | 1.09 | 1.09
 | 0039299027 | CONN HEADER VERT 2POS 4.2MM VERT MINIFIT JR | J201 | 1 | Molex | 39-29-9027 | Volume Production | Digi-Key | WM3875-ND | 0.79 | 0.79
 | 0039299062 | CONN HEADER VERT 6POS 4.2MM VERT MINIFIT JR | J202, J204, J205, J206, J208 | 5 | Molex | 39-29-9062 | Volume Production | Digi-Key | WM7326-ND | 1.15 | 5.75
 | 0039299086 | CONN HEADER VERT 8POS 4.2MM VERT MINIFIT JR | J203, J207 | 2 | Molex | 39-29-9086 | Volume Production | Digi-Key | 23-0039299086-ND | 2.07 | 4.14
 | 0022232041 | CONN HEADER VERT 4POS 2.54MM | J209 | 1 | Molex | 022232041 | Volume Production | Digi-Key | WM4202-ND | 0.35 | 0.35
 | 2mH @ 10kHz 10A 20mOhm | CMC 2MH 10A 2LN TH | L1 | 1 | KEMET | SC-10-E200H | Unknown | Digi-Key | 399-SC-10-E200H-ND | 7.07 | 7.07
 | 1.5uH 11A 10mOhm | FIXED IND 1.5UH 11A 10 MOHM SMD | L2, L10, L19 | 3 | Bourns | SRP6540-1R5M | Volume Production | Digi-Key | SRP6540-1R5MCT-ND | 1.39 | 4.17
 | 4A 470 Ohms @ 100MHz 1206 | FERRITE BEAD 470 OHM 1206 1LN | L3, L4, L6, L15, L16, L20, L21, L24, L25 | 9 | Murata | BLM31KN471SN1L | Volume Production | Digi-Key | 490-16530-1-ND | 0.254 | 2.54
 | 15UH 5.8A | FIXED IND 15UH 5.8A 32 MOHM SMD | L5, L14, L18, L23, L27 | 5 | Bourns | SRR1210-150M | Volume Production | Digi-Key | SRR1210-150MCT-ND | 1.26 | 6.3
 | 1kohm @ 100kHz 6A 14mOhm | CMC 6A 2LN 1K OHM SMD | L7, L9, L13, L17, L22, L26 | 6 | TDK | ACM1211-102-2PLTL01 | Volume Production | Digi-Key | 445-2213-1-ND | 2.04 | 12.24
 | 6A 120 Ohms @ 100MHz 1206 | FERRITE BEAD 120 OHM 1206 1LN | L8, L11, L12 | 3 | Vishay Dale | ILHB1206ER121V | Volume Production | Digi-Key | 541-2304-1-ND | 0.19 | 0.57
 | AON6262E | MOSFET N-CH 60V 40A 8DFN | M2, M3 | 2 | Alpha & Omega Semiconductor | AON6262E | Volume Production | Digi-Key | 800-3747-1-ND | 1.08 | 2.16
 | 4.7kΩ 1% | RES 4.7K OHM 1% 1/10W 0603 | R1, R6, R57, R62, R72 | 5 | Yageo | RC0603FR-074K7L | Volume Production | Digi-Key | 311-4.70KHRCT-ND | 0.019 | 0.19
 | 10kΩ 1% | RES SMD 10K OHM 1% 1/10W 0603 | R2, R5, R7, R11, R16, R25, R46, R47, R48, R50, R51, R52, R54, R59, R61, R63, R64, R69, R71, R73, R74, R81, R84, R85, R86, R96, R98, R100, R106, R109, R111, R121, R124, R126, R128, R129 | 36 | Yageo | RC0603FR-0710KL | Volume Production | Digi-Key | 311-10.0KHRCT-ND | 0.0112 | 0.56
 | 5mΩ 1% 2W | RES 0.005 OHM 1% 2W 2512 | R3, R55, R65, R76, R91, R102, R117 | 7 | Stackpole Electronics | CSNL2512FT5L00 | Volume Production | Digi-Key | CSNL2512FT5L00CT-ND | 0.59 | 4.13
 | 100kΩ 1% | RES 100K OHM 1% 1/10W 0603 | R4, R9, R56, R60, R66, R70, R80, R95, R110, R125 | 10 | Yageo | RC0603FR-07100KL | Volume Production | Digi-Key | 311-100KHRCT-ND | 0.019 | 0.19
 | 5.6 1% 0.25W | RES 5.6 OHM 1% 1/4W 1206 | R8, R75, R90, R101, R116 | 5 | Yageo | RC1206FR-075R6L | Volume Production | Future Electronics | 8144560 | 0.0089 | 44.5
 | 2kΩ 1% | RES 2K OHM 1% 1/10W 0603 | R10, R23, R24, R103, R118 | 5 | Yageo | RC0603FR-072KL | Volume Production | Digi-Key | 311-2.00KHRCT-ND | 0.019 | 0.19
 | 140kΩ 1% | RES SMD 140K OHM 1% 1/10W 0603 | R12, R104, R119 | 3 | Yageo | RT0603FRE07140KL | Volume Production | Digi-Key | 13-RT0603FRE07140KLCT-ND | 0.1 | 0.3
 | 47Ω 1% | RES 47 OHM 1% 1/10W 0603 | R13, R79, R94, R105, R120 | 5 | Yageo | RC0603FR-0747RL | Volume Production | Digi-Key | 311-47.0HRCT-ND | 0.019 | 0.19
 | 180kΩ 5% | RES 180K OHM 5% 1/10W 0603 | R14 | 1 | Yageo | RC0603JR-07180KL | Volume Production | Digi-Key | 311-180KGRCT-ND | 0.1 | 0.1
 | 30kΩ 1% | RES 30K OHM 1% 1/10W 0603 | R15, R108, R123 | 3 | Yageo | RC0603FR-0730KL | Volume Production | Digi-Key | 311-30.0KHRCT-ND | 0.019 | 0.19
 | 330Ω 1% | RES 330 OHM 1% 1/10W 0603 | R17, R20 | 2 | Yageo | RC0603FR-07330RL | Volume Production | Digi-Key | 311-330HRCT-ND | 0.019 | 0.19
 | 562Ω 1% | RES 562 OHM 1% 1/10W 0603 | R18, R21, R77, R92 | 4 | Yageo | RC0603FR-07562RL | Volume Production | Digi-Key | 311-562HRCT-ND | 0.019 | 0.19
 | 1kΩ 1% | RES 1K OHM 1% 1/10W 0603 | R19, R22, R131 | 3 | Yageo | RC0603FR-071KL | Volume Production | Digi-Key | 311-1.00KHRCT-ND | 0.019 | 0.19
 | DNP | RESISTOR NOT POPULATED 0603 | R26, R27, R28, R35, R36, R37, R38, R39, R44, R45 | 10
 | 0 1% 0603 | RES 0 JUMPER 1/10W 0603 | R29, R30, R31, R32, R33, R34, R40, R41, R42, R43, R114, R115 | 12 | Yageo | RC0603FR-070RL | Volume Production | Newark | 50Y7761 | 0.002 | 0.024
 | 10Ω 5% | RES 10 OHM 1% 1/10W 0603 | R58, R68 | 2 | Yageo | RC0603FR-0710RL | Volume Production | Digi-Key | 311-10.0HRCT-ND | 0.1 | 0.2
 | 53.6kΩ 1% | RES 53.6K OHM 1% 1/10W 0603 | R78, R93 | 2 | Yageo | RC0603FR-0753K6L | Volume Production | Digi-Key | 311-53.6KHRCT-ND | 0.019 | 0.19
 | 200kΩ 5% | RES 200K OHM 1% 1/10W 0603 | R82 | 1 | Yageo | RC0603JR-07200KL | Volume Production | Digi-Key | 311-200KGRCT-ND | 0.1 | 0.1
 | 15kΩ 1% | RES 15K OHM 1% 1/10W 0603 | R83, R99 | 2 | Yageo | RC0603FR-0715KL | Volume Production | Digi-Key | 311-15.0KHRCT-ND | 0.019 | 0.19
 | 169kΩ 1% | RES 169K OHM 1% 1/10W 0603 | R97 | 1 | Yageo | RC0603FR-07169KL | Volume Production | Digi-Key | 311-169KHRCT-ND | 0.1 | 0.1
 | 184kΩ 1% | RES 184K OHM 0.5% 1/10W 0603 | R107 | 1 | Yageo | RT0603DRE07184KL | Unknown | Digi-Key | 13-RT0603DRE07184KLCT-ND | 0.1 | 0.1
 | 187kΩ 1% | RES 187K OHM 1% 1/10W 0603 | R122 | 1 | Yageo | RC0603FR-07187KL | Volume Production | Digi-Key | 311-187KHRCT-ND | 0.1 | 0.1
 | 90.9kΩ 1% | RES 90.9K OHM 1% 1/10W 0603 | R127 | 1 | Yageo | RC0603FR-0790K9L | Volume Production | Digi-Key | 311-90.9KHRCT-ND | 0.1 | 0.1
 | 1.69kΩ 1% | RES 1.69K OHM 1% 1/10W 0603 | R130 | 1 | Yageo | RC0603FR-071K69L | Volume Production | Digi-Key | 311-1.69KHRDKR-ND | 0.1 | 0.1
 | Tact SPST | SWITCH TACT vertical SMD | SW1 | 1 | ITT C&K | PTS645SM43SMTR92LFS | Volume Production | Newark | 95W3587 | 0.18 | 0.18
 | MAX4372FEUK+T | IC CURR SENSE 1 CIRCUIT SOT23-5 | U1, U22, U24, U26, U28, U31, U33 | 7 | Analog Devices | MAX4372FEUK+T | Unknown | Digi-Key | MAX4372FEUK+TTR-ND
 | NCS21911SN2T1G | IC OPAMP ZERO-DRIFT 1 CIRC 5TSOP | U2, U29, U34, U35, U36, U37, U38 | 7 | ON Semiconductor | NCS21911SN2T1G | Volume Production | Digi-Key | NCS21911SN2T1GOSCT-ND | 2.59 | 18.13
 | PCA9517AD,118 | IC REDRIVER I2C 1CH 400KHZ 8SO | U3 | 1 | NXP Semiconductors | PCA9517AD,118 | Volume Production | Digi-Key | 568-5927-1-ND | 1.72 | 1.72
 | MIC5235YM5-TR | IC REG LINEAR 150MA MICROCAP LDO | U4 | 1 | Microchip | MIC5235YM5TR | Obsolete | Digi-Key | 576-1284-6-ND | 1.35 | 1.35
 | LM3880MF-1AB/NOPB | IC PWR SUPPLY SEQUENCER SOT23-6 | U6, U8 | 2 | Texas Instruments | LM3880MF-1AB/NOPB | Volume Production | Digi-Key | LM3880MF-1AB/NOPBCT-ND | 1.56 | 3.12
 | SN74LVC2G157DCTR | IC MULTIPLEXER 1 X 2:1 SM8 | U7, U9 | 2 | Texas Instruments | SN74LVC2G157DCTR | Volume Production | Digi-Key | 296-13266-1-ND | 0.5 | 1
 | SN74AHC1G08DBVR | IC GATE AND 1CH 2-INP SOT23-5 | U10 | 1 | Texas Instruments | SN74AHC1G08DBVR | Volume Production | Digi-Key | 296-1091-1-ND | 0.33 | 0.33
 | SN74AHC1GU04DBVR | IC INVERTER 1CH 1-INP SOT23-5 | U11 | 1 | Texas Instruments | SN74AHC1G86DBVR | Volume Production | Digi-Key | 296-1094-1-ND | 0.3 | 0.3
 | SN74LVC1G332DCKR | IC GATE OR 1CH 3-INP SC70-6 | U12 | 1 | Texas Instruments | SN74LVC1G332DCKR | Volume Production | Digi-Key | 296-15943-1-ND | 0.5 | 0.5
 | SN74AHCT08PW | IC GATE AND 4CH 2-INP 14TSSOP | U13, U14 | 2 | Texas Instruments | SN74AHCT08PW | Volume Production | Digi-Key | 296-33685-5-ND | 1.1 | 2.2
 | MCP1316MT-20LI/OT | IC SUPERVISOR 1 CHANNEL SOT23-5 | U15 | 1 | Microchip | MCP1316MT-20LI/OT | Volume Production | Digi-Key | MCP1316MT-20LI/OTCT-ND | 0.86 | 0.86
 | TPS54540BDDA | IC REG BUCK ADJUSTABLE 5A 8SOPWR | U16, U25, U27, U30, U32 | 5 | Texas Instruments | TPS54540BDDA | Volume Production | Digi-Key | 296-TPS54540BDDA-ND | 5.44 | 27.2
 | LM317MKVURG3 | IC REG LIN POS ADJ 500MA TO252-3 | U17, U18 | 2 | Texas Instruments | LM317MKVURG3 | Volume Production | Digi-Key | 296-19495-1-ND
 | ADS7828EB/2K5 | IC ADC 12BIT SAR 16TSSOP | U19, U20 | 2 | Texas Instruments | ADS7828EB/2K5 | Volume Production | Digi-Key | 296-41194-1-ND
 | RT1720GF | IC HOT SWAP CTRLR GP 10MSOP | U21, U23 | 2 | Richtek | RT1720GF | Volume Production | Digi-Key | 1028-1445-1-ND | 1.62 | 3.24
 | DNP | DNP | U39 | 1
 | PCA9535APW,118 | IC I/O EXPANDER I2C 16B 24TSSOP | U800, U801 | 2 | NXP Semiconductors | PCA9535APW,118 | Volume Production | Digi-Key | 568-9913-1-ND | 2.38 | 4.76

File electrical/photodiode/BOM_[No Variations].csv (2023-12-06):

Name | Description | Designator | Part Number | Price | Qty
0.1 uF_0 | 0.1 µF ±10% 25V Ceramic Capacitor X7R 0805 (2012 Metric) | C100, C105, C109, C111 |  |  | 4
1.0 uF_1 | 1 µF ±10% 25V Ceramic Capacitor X7R 0805 (2012 Metric) | C101 |  |  | 1
CAP_0805_6 | 5 pF ±0.25pF 16V Ceramic Capacitor C0G, NP0 0805 (2012 Metric) | C113 |  |  | 1
ODD-3W-2_7 | SENSOR PHOTODIODE 940NM TO5 | D112 |  |  | 1
644456-2_8 | 644456-2_8 | J100 |  |  | 1
221789-1_9 | SMA Connector Jack, Female Socket 50 Ohms Through Hole Solder | J112 |  |  | 1
0_40 | 0 Ohms Jumper Chip Resistor 0805 (2012 Metric) Moisture Resistant Thick Film | R109, R110, R116 |  |  | 3
RES_0805_28 | 12.7 kOhms ±1% 0.125W, 1/8W Chip Resistor 0805 (2012 Metric) Moisture Resistant Thick Film | R111 |  |  | 1
RES_0805_29 | RES_0805_29 | R115 |  |  | 1
RES_0805_31 | 50 Ohms ±0.1% 0.125W, 1/8W Chip Resistor 0805 (2012 Metric) Moisture Resistant Thin Film | R120 |  |  | 1
1.0 uF 25 V_36 | 1 µF Molded Tantalum Capacitors 25 V 0805 (2012 Metric) 11Ohm @ 100kHz | T100, T105, T108, T109, T111 |  |  | 5
MIC5203-5.0BM5-TR_42 | Linear Voltage Regulator IC Positive Fixed 1 Output 80mA SOT-23-5 | U100 |  |  | 1
SI7661ESA+_37 | Charge Pump Switching Regulator IC Positive or Negative Fixed -Vin, 2Vin 1 Output 20mA 8-SOIC (0.154\ | 3.90mm Width)" | U105 |  |  | 1
LTC6268_38 | LTC6268_38 | U111 |  |  | 1

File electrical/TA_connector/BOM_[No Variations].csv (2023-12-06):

Line # | Name | Description | Designator | Revision ID | Revision Status | Quantity | Manufacturer 1 | Manufacturer Part Number 1 | Manufacturer Lifecycle 1 | Supplier 1 | Supplier Part Number 1 | Supplier Unit Price 1 | Supplier Subtotal 1
 | Azimuth 5250-100-7S | Azimuth 5253-100-7-S Standard | J1 |  |  | 1 | Molex | 22-23-2061 | Volume Production | Digi-Key
 | Azimuth 5253-100-7R | Azimuth 5253-100-7R reversed | J2 |  |  | 1 | Molex | 22-23-2061 | Volume Production | Digi-Key
 | IPL1-108-01-L-D-K | Connector Header Through Hole 16 position 0.100\",J3" |  |  | 1 | Samtec | IPL1-108-01-L-D-K | Volume Production | Digi-Key | SAM10585-ND | 2.29 | 2.29

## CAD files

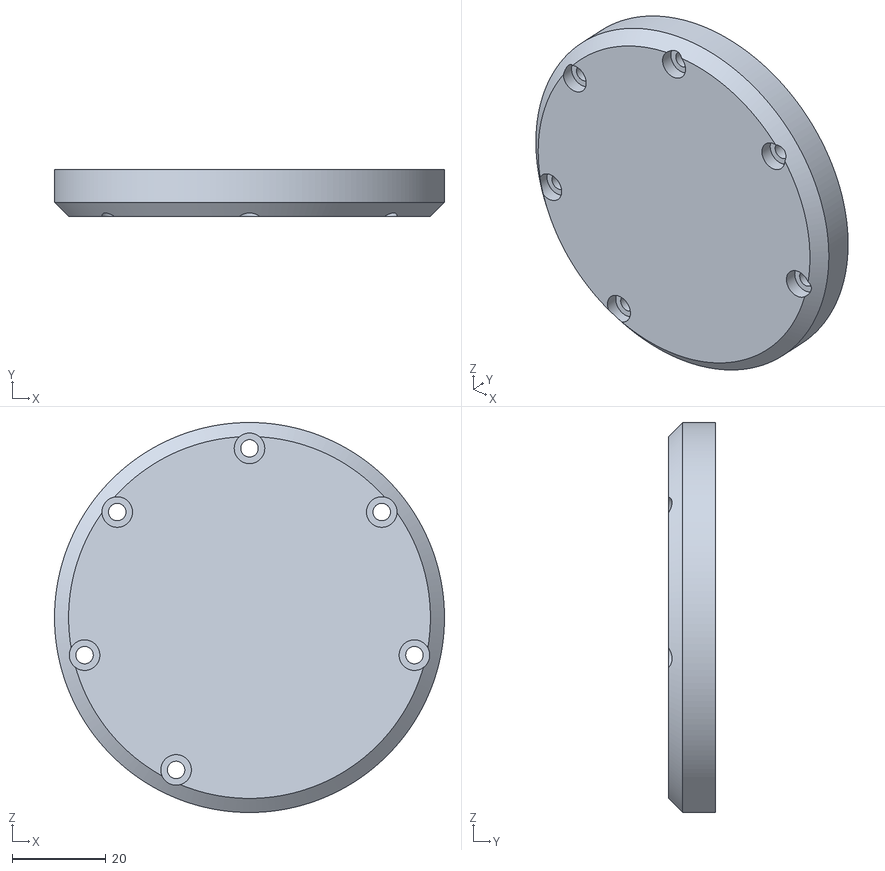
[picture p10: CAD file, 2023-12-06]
mechanical/stl/3000-0654 - ADAPTER, LASER TIP ASSEMBLY TO OPHIR, BACK PLATE - R01.STL
83.0 x 10.00 x 83.0

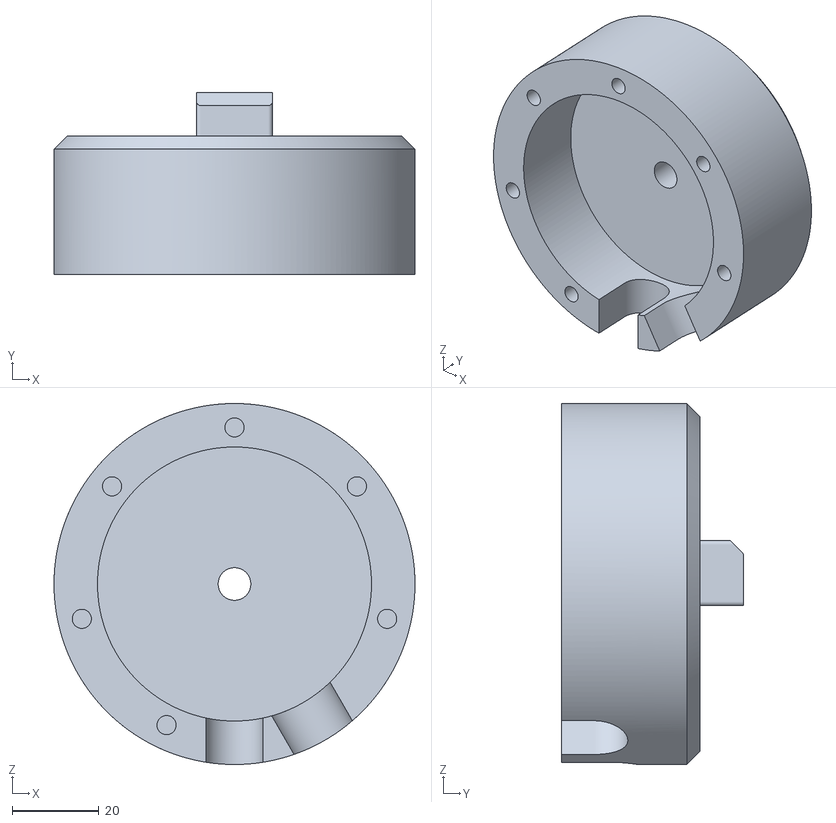
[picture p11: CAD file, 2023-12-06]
mechanical/stl/3000-0653 - ADAPTER, LASER TIP ASSEMBLY TO OPHIR, MAIN BODY - R01.STL
83.0 x 41.8 x 83.0

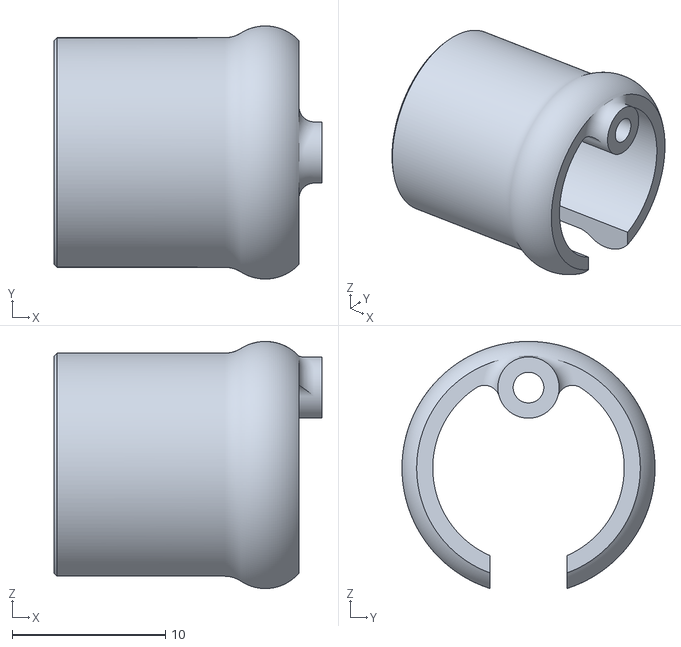
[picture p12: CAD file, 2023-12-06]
mechanical/stl/3000-0497 - MAIN SHEATH STOP - R02.STL
17.5 x 16.5 x 16.1

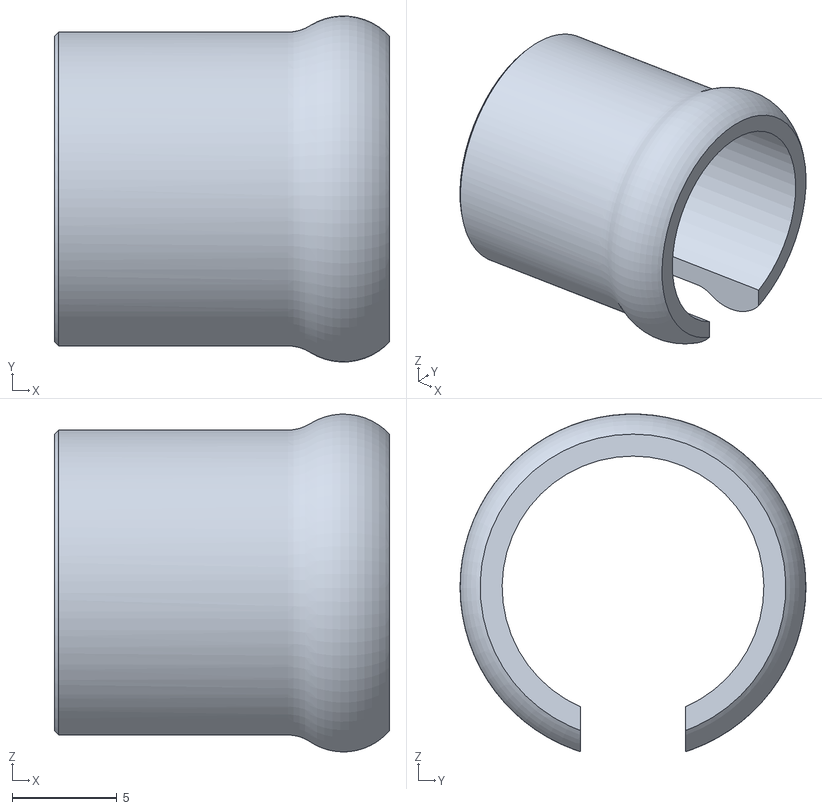
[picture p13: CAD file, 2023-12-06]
mechanical/stl/3000-0497 - MAIN SHEATH STOP - R01.STL
16.0 x 16.5 x 16.1

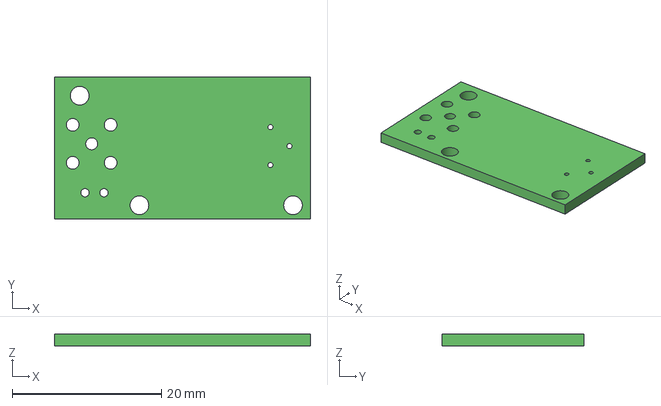
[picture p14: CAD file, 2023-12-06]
electrical/photodiode/STEP_[No Variations] for 7000-0278 PCA-Photodiode-REV 03.PcbDoc.step
34.3 x 19.1 x 1.57 mm

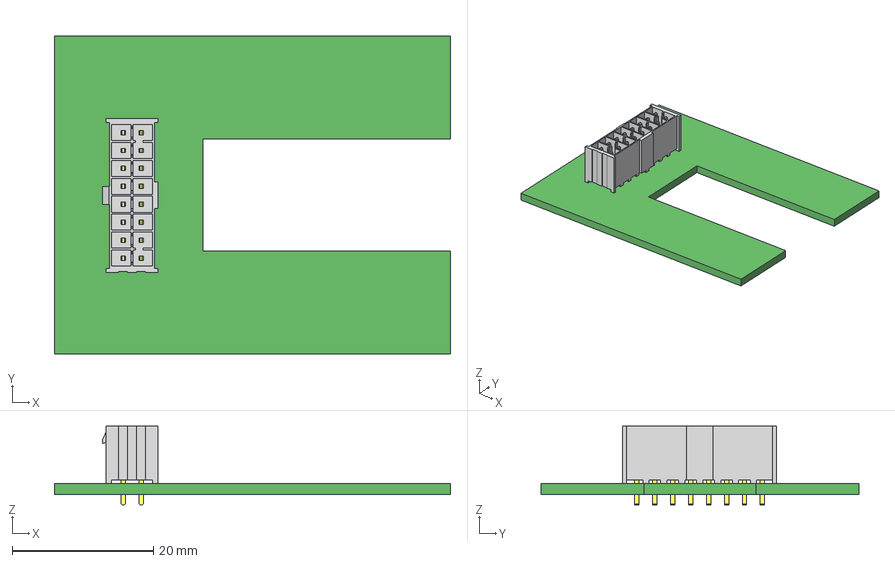
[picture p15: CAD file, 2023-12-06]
electrical/TA_connector/STEP_[No Variations] for 7000-0133 Rev 02-PCB, TA Mount2.PcbDoc.step
56.1 x 45.1 x 11.2 mm
T-1S64-01-08-D
IPL1-108-01-D-K_HDR

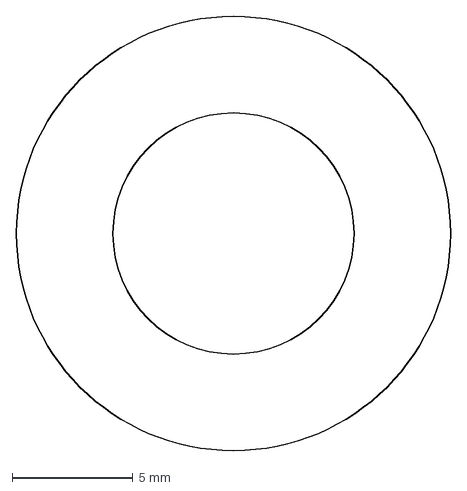
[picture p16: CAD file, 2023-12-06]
mechanical/dxf/3000-0611 - FOAM PAD, MCA RING - R02.DXF
18.0 x 18.0 mm

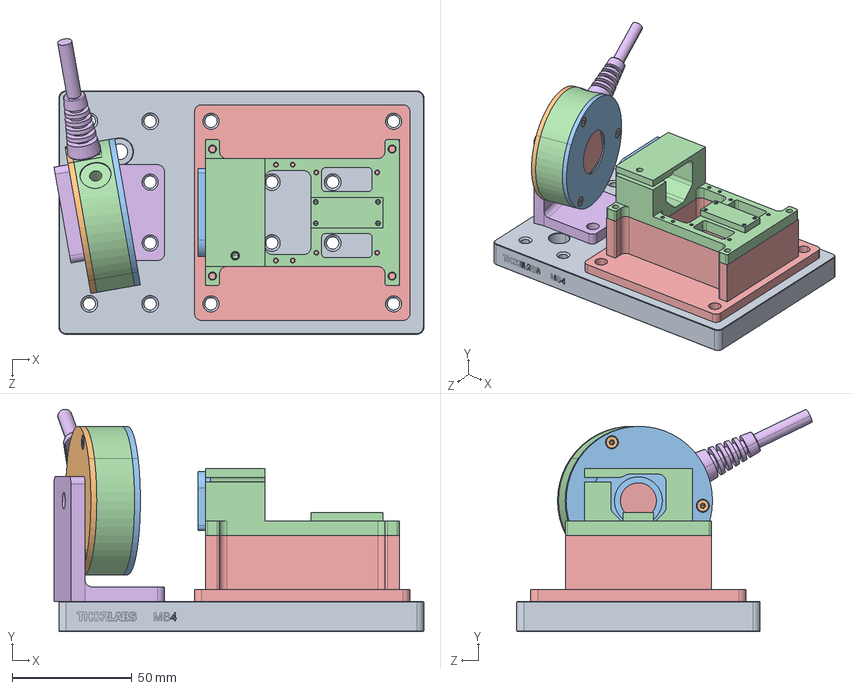
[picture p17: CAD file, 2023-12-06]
mechanical/major_subs/source_module/7000-0272.STEP
154.4 x 92.8 x 123.4 mm
ophir head

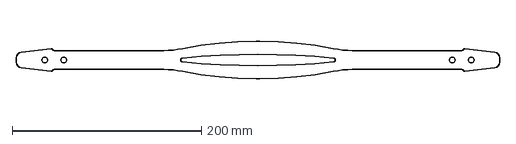
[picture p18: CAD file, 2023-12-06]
mechanical/dxf/3000-0541 - STRAP, HEADSET, LONG - R01 - DXF.dxf
510.0 x 40.0 mm

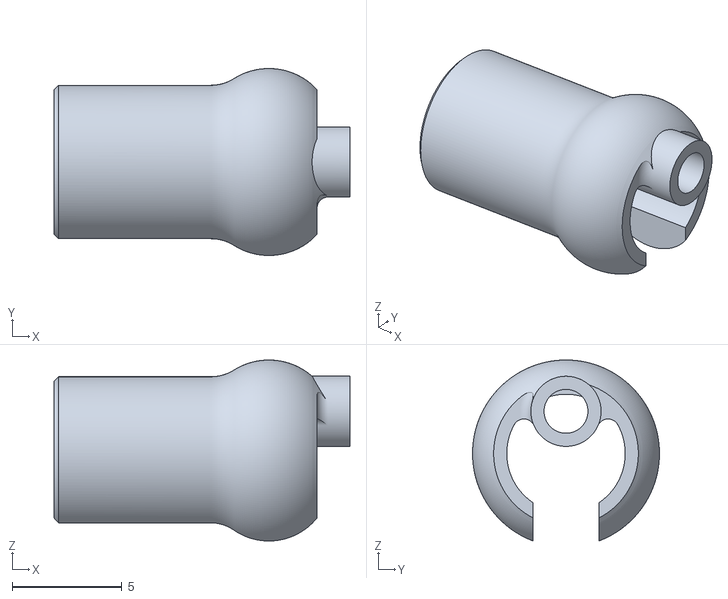
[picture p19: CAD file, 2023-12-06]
mechanical/stl/3000-0498 - MODULE SHEATH STOP - R02.STL
13.5 x 8.53 x 8.25

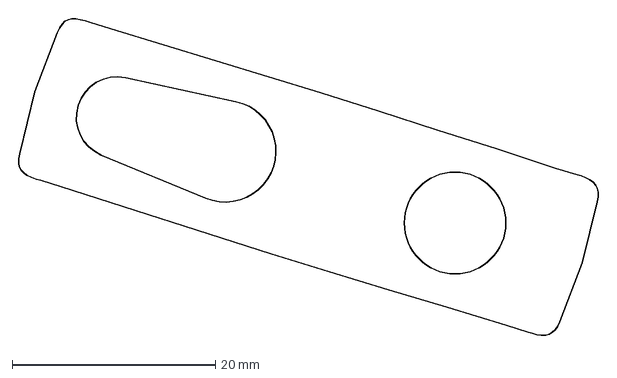
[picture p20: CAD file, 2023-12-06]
mechanical/dxf/3000-0608 - FOAM PAD, HORIZONTAL, 34 MM FAR S-D DISTANCE - R01.DXF
57.5 x 31.6 mm

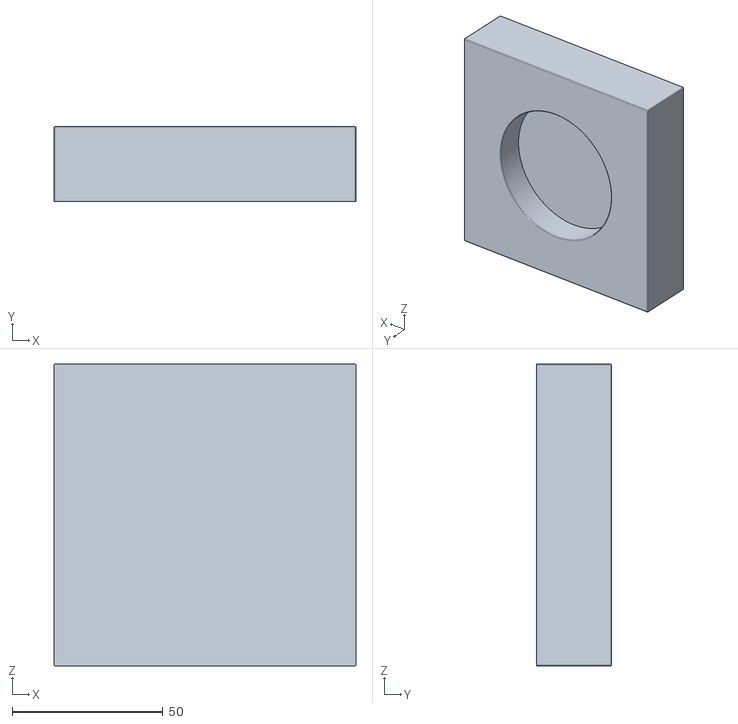
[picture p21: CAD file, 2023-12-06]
mechanical/stl/3000-0635 - FIXTURE, CAMERA OPTIC EPOXY APPLICATION, BASE - R01.STL
100.0 x 25.0 x 100.0

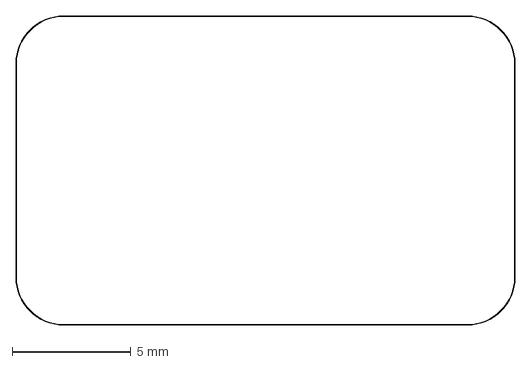
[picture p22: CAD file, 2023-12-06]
mechanical/dxf/3000-0609 - FOAM PAD, VERTICAL, 34 MM FAR S-D DISTANCE - R01.DXF
21.0 x 13.0 mm

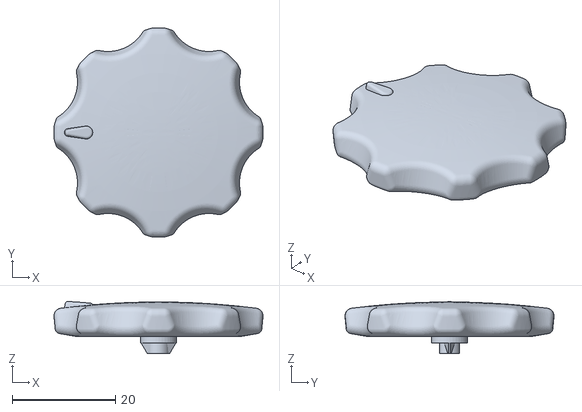
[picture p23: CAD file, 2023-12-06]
mechanical/stl/3000-0518 - DIAL - R01.STL
40.6 x 40.6 x 10.1

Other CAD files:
mechanical/stl/7000-0235 - VISOR ASSEMBLY, GEN 2.5 - R01.STL
mechanical/major_subs/console_assembly/7000-0246.STEP
mechanical/dxf/3000-0543 - STRAP, HEADSET, SHORT - R02 - DXF.DXF
mechanical/stl/3000-0591 - DETECTOR HOUSING, FAR - R01.STL
mechanical/dxf/3000-0525 - MODULE FACE PAD - R01 - DXF.DXF
mechanical/dxf/3000-0526 - HEADSET SIDE PAD - R01 - DXF.DXF
mechanical/dxf/3000-0542 - STRAP, HEADSET, MEDIUM - R01 - DXF.dxf
mechanical/dxf/3000-0543 - STRAP, HEADSET, SHORT - R01 - DXF.dxf
mechanical/dxf/3000-0609 - FOAM PAD, VERTICAL, 34 MM FAR S-D DISTANCE - R02.DXF
mechanical/dxf/3000-0621 - RETAINING RING, TOOTHED, ROUNDED CORNERS - R01.DXF
mechanical/dxf/3000-0622 - RETAINING RING, SPLIT, TOOTHED - R01.DXF
mechanical/dxf/3000-0623 - RETAINING RING, SPLIT - R01.DXF
mechanical/dxf/3000-0626 - RETAINING RING, SPIKED - R01.DXF
mechanical/stl/3000-0479 - POLE CLAMP - R01.STL
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

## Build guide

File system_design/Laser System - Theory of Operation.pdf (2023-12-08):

# High Level Summary

The laser system consists of a seed laser, an amplifier, a laser isolator, and two thermoelectric coolers to keep the lasers cool. The seed laser turns on and is active all the time and the amplifier, also known as the TA or tapered amplifier, pulses in sync with the camera. Each of these devices, with the exclusion of the isolator, has a control module. On newer versions of the system the isolator is built in to the laser components. The Multifunction Laser Board, or MLB/MLIB powers the two laser controllers and controls the thermoelectric coolers. The MLIB monitors the lasers and shuts them down if various parameters are breached. The MLIB also connects to a small board that is mounted atop the TA that monitors the laser’s instantaneous power.

# Block Diagram

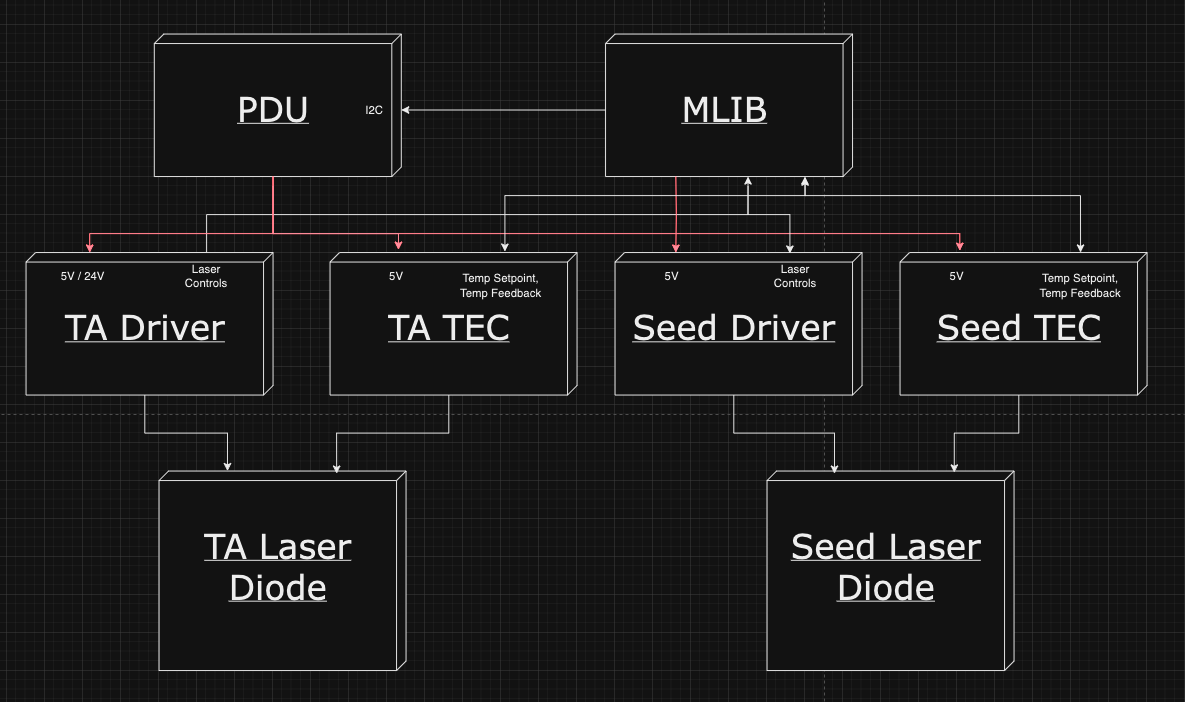
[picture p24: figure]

# Parts and Part Numbers

Name | Part Number | Link
Seed Laser Diode | FPV785P | https://punchout.webdev02.thorlabs.com/thorproduct.cfm?partnumber=F PV785P (https://punchout.webdev02.thorlabs.com/thorproduct.cfm?partnumber=FPV785P)
TA | TPA780P20 | https://www.thorlabs.com/thorproduct.cfm?partnumber=TPA780P20
Seed Driver | MPL500 | https://www.teamwavelength.com/product/mpl500-laser-diode-driver/
TA Driver | LD10CHA | https://www.teamwavelength.com/product/ld10cha-10-a-30-v-laser-diode-
driver/ (https://www.teamwavelength.com/product/ld10cha-10-a-30-v-laser-diode-driver/)
Seed TEC | WTC3293 | https://www.teamwavelength.com/download/Datasheets/wtc3243.pdf
TA TEC | WTC3293 | https://www.teamwavelength.com/download/Datasheets/wtc3243.pdf

## Component Configurations

### MPL500

The MPL500 runs in constant current mode with the onboard trimpots tuned to offer no offset to MOD_INPUT and to limit the current to the diode at 200mA. Each MPL500 that has its trimpots tuned should have them taped over and signed off on to prevent accidental modification.

The photodiode is not required in this mode and instead of being connected to the MPL500 it is routed directly to the laser safety board. Note that in constant power mode, the photodiode is required.

In normal operation, the ENABLE pin is pulled high and the MOD_INPUT pin is set to 1.5V. This voltage corresponds to 150mA to the seed, or 10mW.

### TA Driver

The LD10CHA runs in constant current mode without a photodiode, similar to the MPL500. It also runs in dual power supply mode with 5V and 24V supplied. It has its trimpots set to add nothing to MOD_INPUT and limit the laser current to 6A.

To enable this configuration, the system should have JP1 and JP2 pulled before beginning operation. JP3 can be removed or not since a photodiode is not connected. The setpoint trimpot may be turned all the way to CCW until a click is heard to zero it, and the limit trimpot may be set to 6A by looking at the CURR_LIM voltage feedback. The switches must be configured for Constant Current.

# Normal Operation

In normal operation, the seed will be turned on at startup and remain on until the system is powered down. When the laser needs to pulse for a scan, the TA is enabled and the TA’s MOD_INPUT is pulsed with a voltage proportional to the intended laser power.

Nominally, the laser system goes through the following steps:
1. Turn on Seed
a. Set Seed En = 1
b. Set MOD_INPUT = 1.5V (150mA)
2. Reset Error Registers
3. Enable TA
a. Set TA ENABLE = 0
4. Pulse TA
a. Pulse MOD_INPUT at 40Hz, 250us time on, at 5V to get 5A per pulse
5. Disable TA
a. Set TA_ENABLE = 1
6. Turn off Seed
a. Set SEED_EN = 0

# Fault List

The laser system has 10 different signals that must be within range in order to allow the TA to be enabled. Those are:
- ESTOP OK
- TA_ENABLE
- Seed Current OK
- Seed Photodiode OK
- TA Current Pulse Length OK
- TA Current Pulse Intensity OK
- TA Current Pulse Frequency OK
- TA Photodiode Pulse Length OK
- TA Photodiode Pulse Intensity OK
- TA Photodiode Pulse Frequency OK

All 10 of these go through a series of AND gates to enable the TA driver. As the TA driver is enabled by a 0V/low signal rather than a high signal, the final AND gate is actually a NAND gate.

Each of these errors has a memory device attached and will hold its state if it trips. A reset is required to reset these memory units. At startup, the system will be in an error state because the seed will be disabled. Once the seed is enabled the system must be reset in order to enable the TA. Alternatively, the threshold may be set such that the TA never turns off due to the activity of the seed and this step may be omitted.

In normal operation, the laser should fire at 40Hz with a pulse width of 250us and a height of 5V. The seed should be given 1.5V.

If the laser breaches 5% of any of these four parameters, the laser system should trip and disable the TA. Documentation about this will be updated here once testing completes.

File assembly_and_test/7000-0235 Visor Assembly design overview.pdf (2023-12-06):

# Openwater

7000-0235

# Visor Assembly Design overview

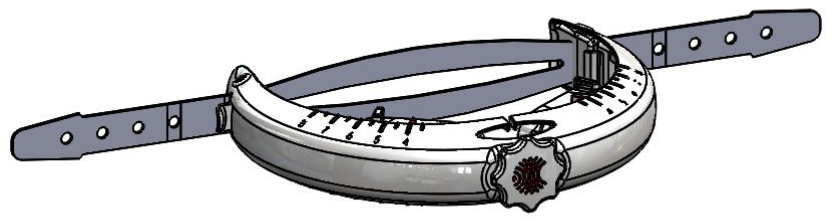
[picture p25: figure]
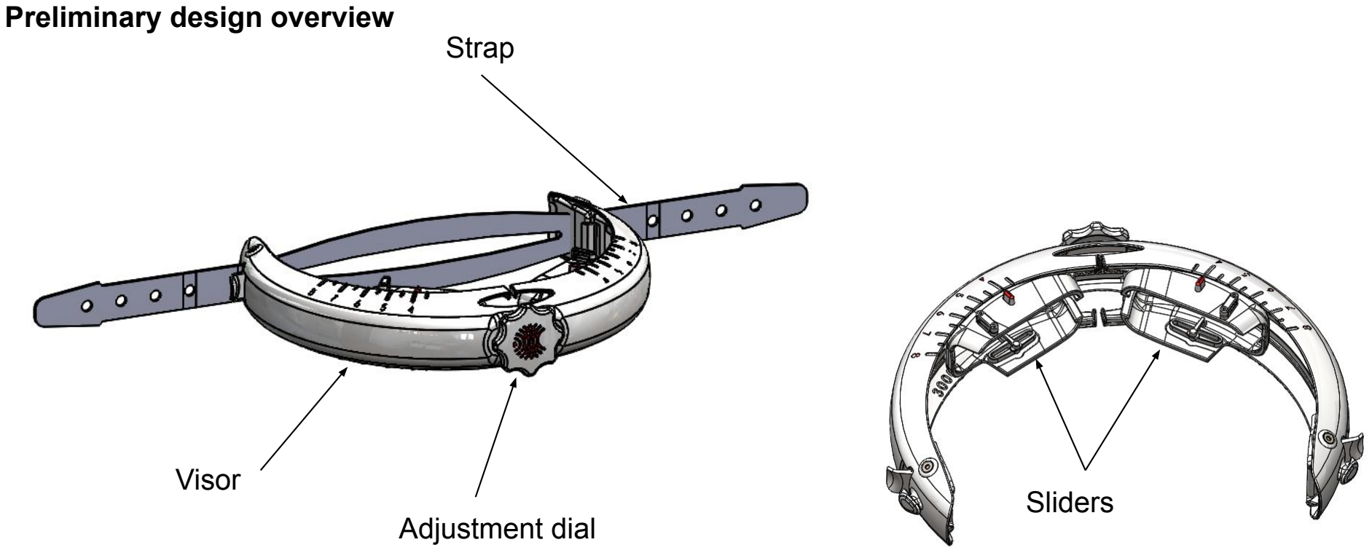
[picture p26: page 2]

Preliminary design overview

Visor

Adjustment dial

Strap

Sliders

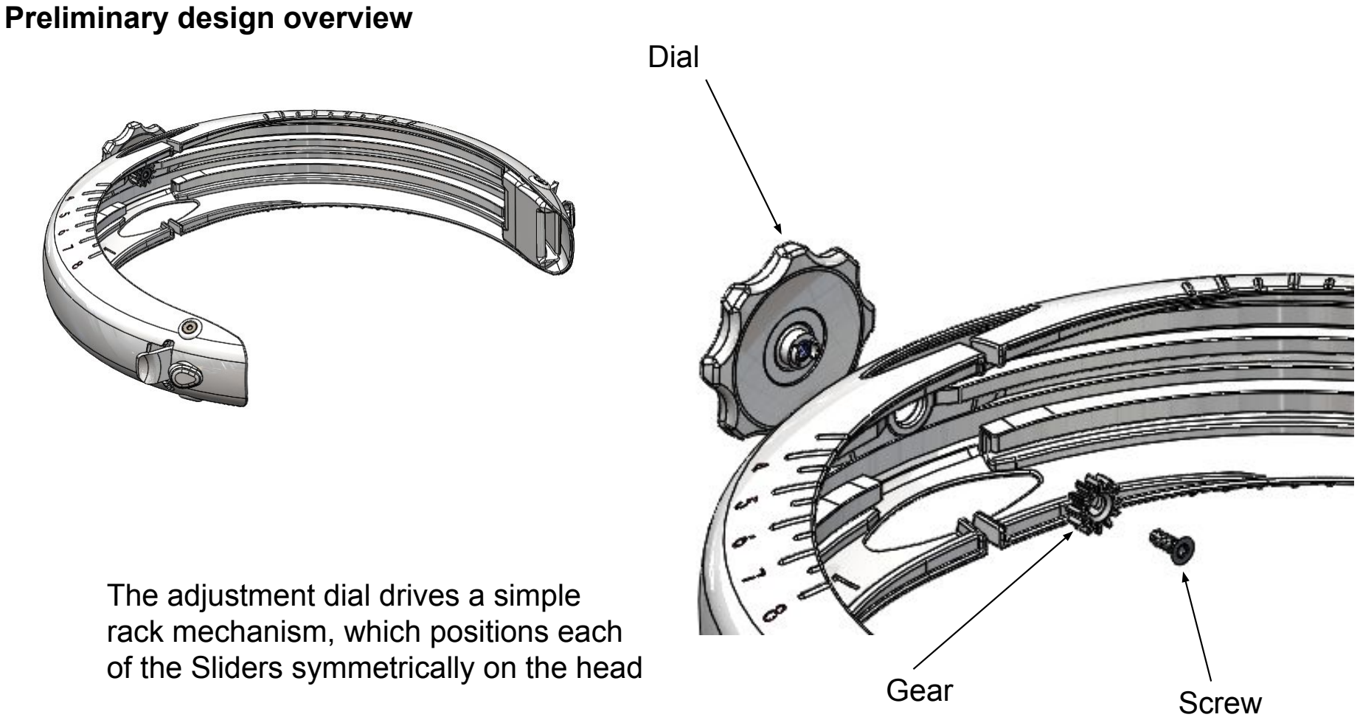
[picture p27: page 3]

Dial

Gear | Screw

The adjustment dial drives a simple rack mechanism, which positions each of the Sliders symmetrically on the head

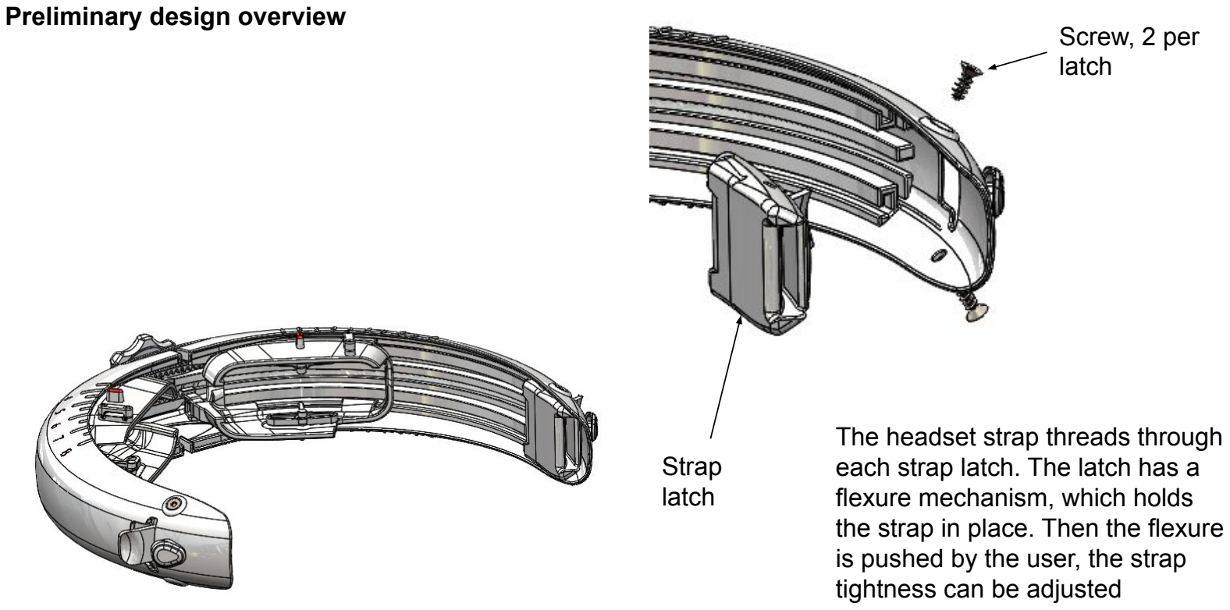
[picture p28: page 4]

Strap
latch

Screw, 2 per
latch

The headset strap threads through each strap latch. The latch has a flexure mechanism, which holds the strap in place. Then the flexure is pushed by the user, the strap tightness can be adjusted

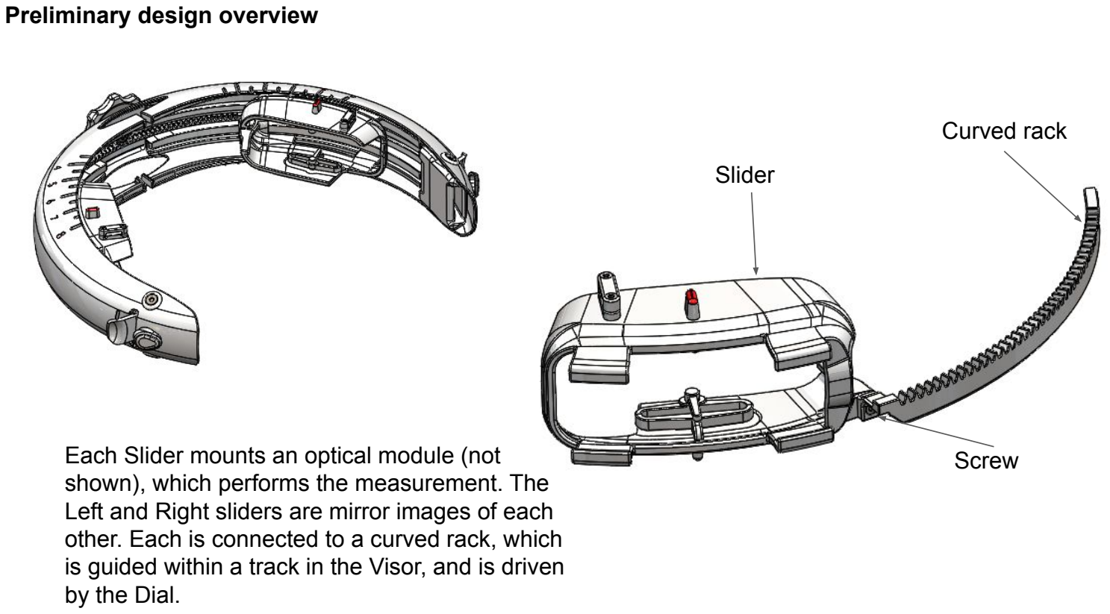
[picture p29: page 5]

Slider

Curved rack

Each Slider mounts an optical module (not | Screw
shown), which performs the measurement. The
Left and Right sliders are mirror images of each
other. Each is connected to a curved rack, which
is guided within a track in the Visor, and is driven by the Dial.

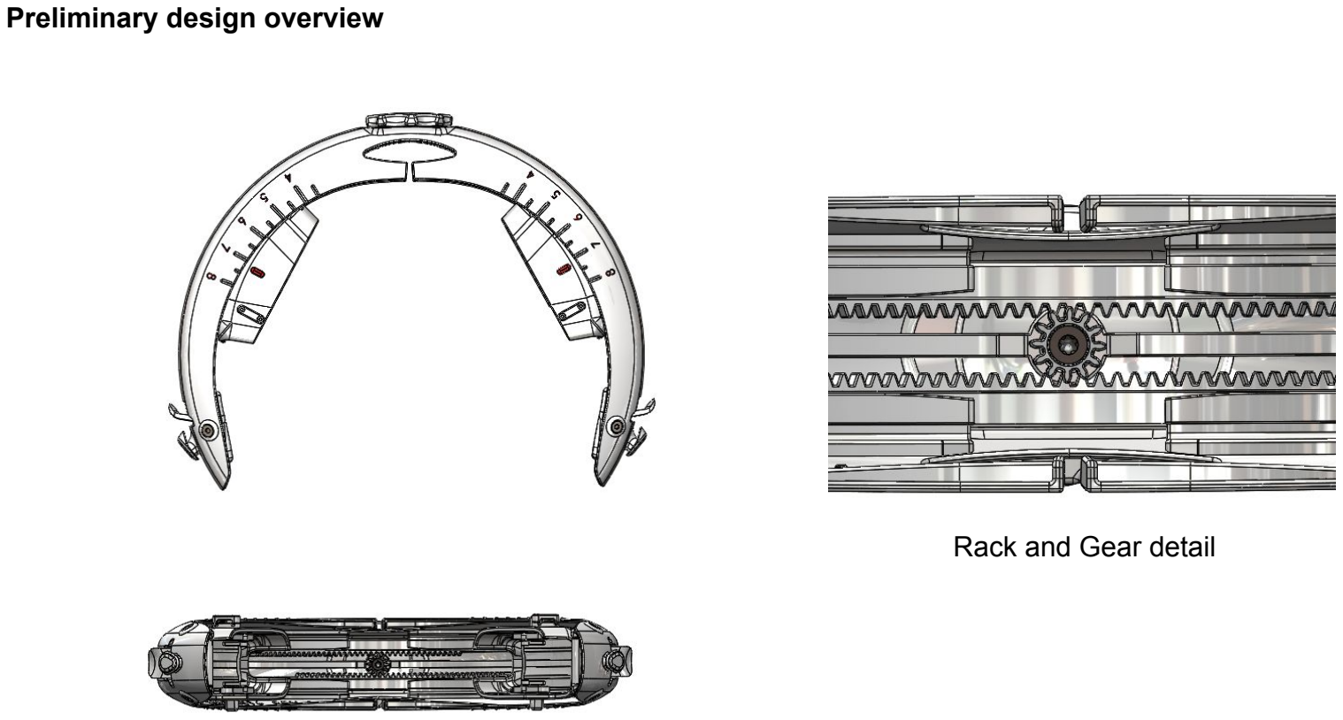
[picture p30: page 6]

Rack and Gear detail

Custom component fabrication summary | Note that part numbers are subject to change
PN | Description | Fabrication method | Material | Finishing
3000-0516 | VISOR | SLS | NYLON 12, WHITE | LEVEL 4 PAINT, SEE DWG
3000-0529 | SLIDER, LEFT, MCA | SLS | NYLON 12, WHITE | LEVEL 4 PAINT, SEE DWG
3000-0535 | CURVED RACK | SLS | NYLON 12, GLASS FILLED | NONE
3000-0522 | CABLE CLAMP | SLS | NYLON 12, WHITE | NONE
3000-0536 | SLIDER, RIGHT, MCA | SLS | NYLON 12, WHITE | LEVEL 4 PAINT, SEE DWG
3000-0640 | STRAP LATCH, LOW PROFILE | SLS | NYLON 12, WHITE | NONE
3000-0661 | GEAR, V2 | SLA | RIGID 4000 | NONE
3000-0662 | DIAL, V2 | SLA | RIGID 4000 | LEVEL 4 PAINT, SEE DWG. INSTALLATION OF 1 THREADED INSERT
3000-0543 | STRAP, HEADSET, SHORT | FLAT PATTERN CUT | 50A SILICONE SHEET | PARYLENE COAT
3000-0664 | HOUSING, AGGREGATOR, BODY | SLS | NYLON 12, WHITE | LEVEL 4 PAINT, SEE DWG
3000-0665 | HOUSING, AGGREGATOR, LID | SLS | NYLON 12, WHITE | LEVEL 4 PAINT, SEE DWG

Inspection

Visual inspection of assembly, e.g. all screws present and torqued, free of damage, all paint intact, no loss of red marks

Check that any module mounting features are still intact (current design has some delicate flexure elements; we may change this before final manufacturing)

Check the adjustment mechanism
- No wobble in dial
- Smooth adjustment with no binding
- Sliders cannot freely fall/slip along the visor (there is some resistance to movement, just enough to keep the assembly stable when it’s not being actively adjusted)

Check the strap latches
- Latches hold the straps secure when pulled
- Straps can slip through the latches when the flexure lever is depressed

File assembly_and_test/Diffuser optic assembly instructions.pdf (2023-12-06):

# diffuser optic assembly instructions

# overview

## Diffuser film is glued directly to the sapphire optic with a thin layer of UV cure CA adhesive, instead of using pressure sensitive adhesive sheet as was done in previous generations of the blood flow device

# Prepare work surface and cutting tool

Wipe down cutter body, cutter pin, and pad with IPA

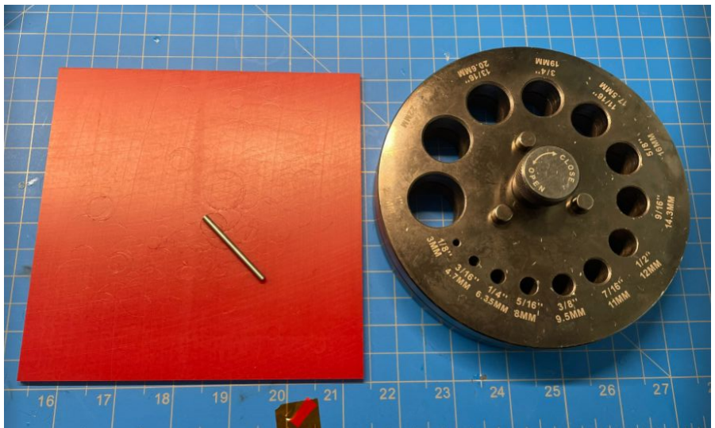
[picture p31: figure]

# Prepare diffuser material strip

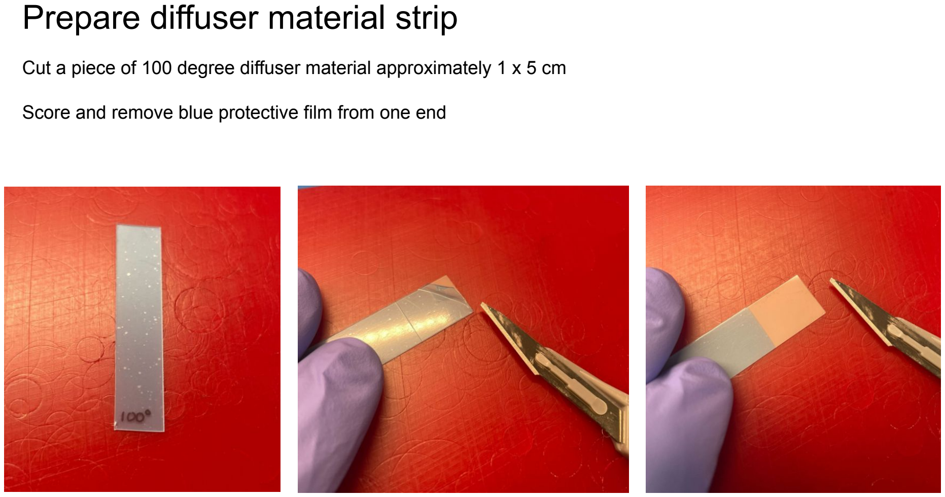
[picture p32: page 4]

Cut a piece of 100 degree diffuser material approximately 1 x 5 cm

Score and remove blue protective film from one end

# Punch diffuser disc

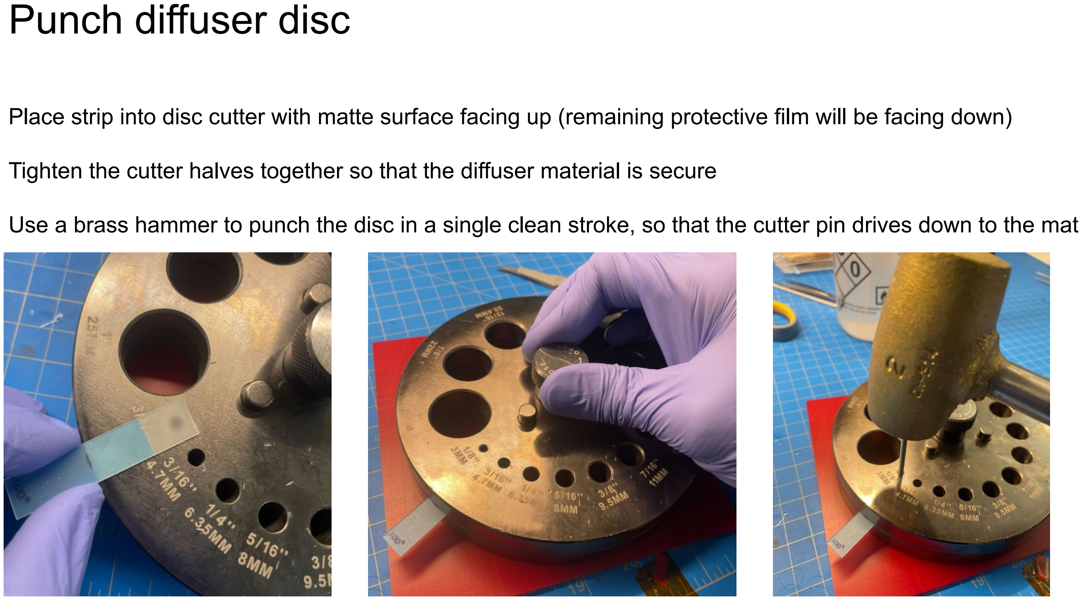
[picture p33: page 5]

Place strip into disc cutter with matte surface facing up (remaining protective film will be facing down)

Tighten the cutter halves together so that the diffuser material is secure

Use a brass hammer to punch the disc in a single clean stroke, so that the cutter pin drives down to the mat

# Prepare diffuser and optic

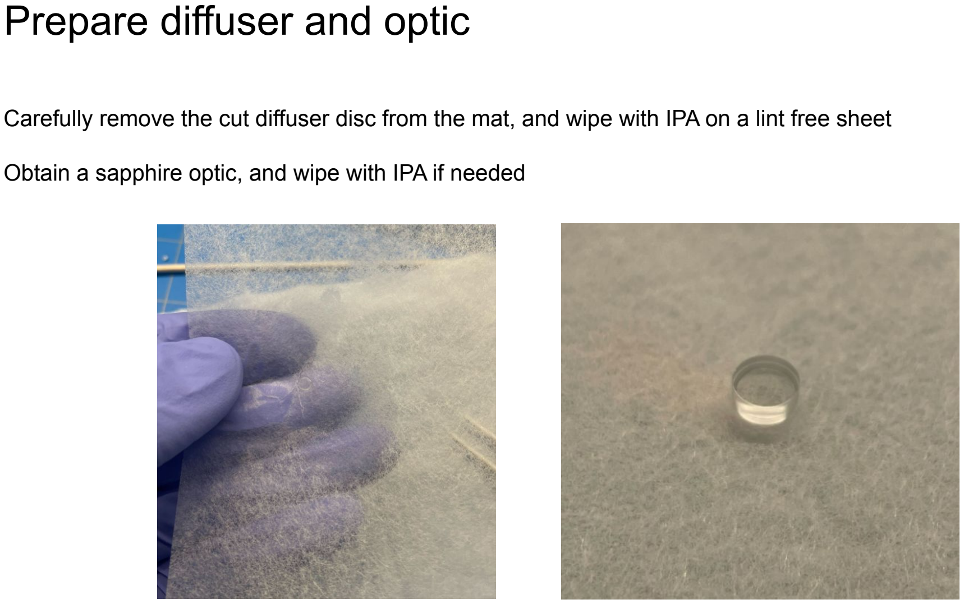
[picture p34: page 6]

Carefully remove the cut diffuser disc from the mat, and wipe with IPA on a lint free sheet

Obtain a sapphire optic, and wipe with IPA if needed

# Glue diffuser disc to optic

Place sapphire optic on lint free sheet with larger diameter facing UP

Use a needle applicator to apply a small amount of Loctite 4310 adhesive to the surface. Spread somewhat evenly across the optic

Carefully place and center the diffuser disc on the optic
When viewing the disc, one side will appear white, while the other appears translucent
Translucent side should be facing UP
If placed incorrectly, the adhesive will wet the diffuser surface and it will appear clear instead of translucent

Lightly press the diffuser disc to the optic, removing air bubbles. Remove tool and cure with UV gun

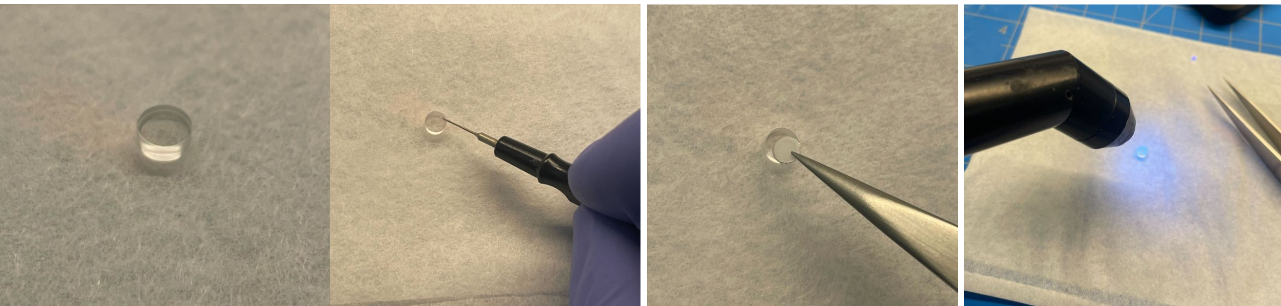
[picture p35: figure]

# Clean and inspect assembly

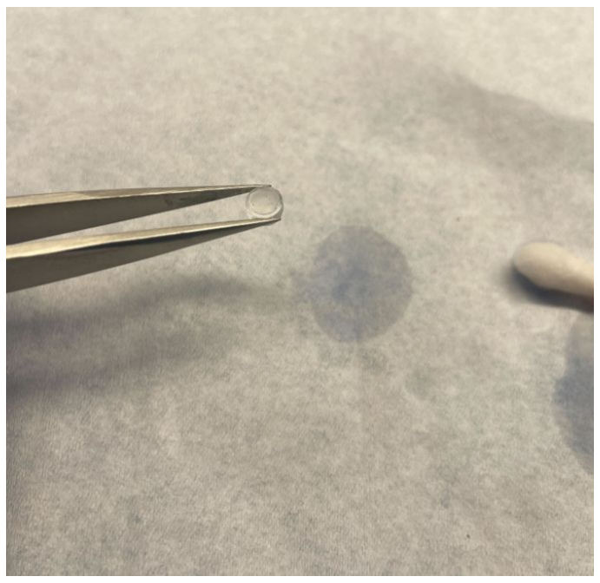
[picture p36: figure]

Wipe assembly with a small amount of IPA and lint free wipe

Inspect and verify that
- Assembly is free of debris
- Diffuser disc is well centered and does not overhang edge of sapphire optic
- Diffuser disc is free of air bubbles
- Diffuser disc appears evenly translucent across its face
- Diffuser is placed on correct side (larger diameter)

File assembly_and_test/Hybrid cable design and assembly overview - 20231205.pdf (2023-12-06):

# Openwater Blood Flow Hybrid Cable Design and assembly overview

High-level process flow

Block diagram
Hybrid cable

Block diagram
Complete 6-cam headset assembly 7000-0185
For reference

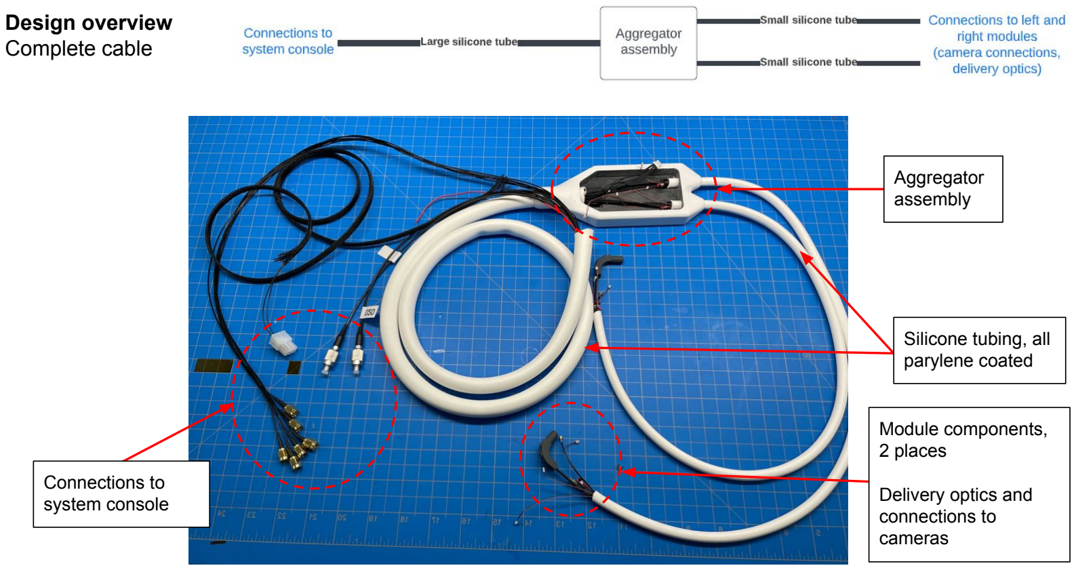
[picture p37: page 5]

Design overview
Complete cable

Connections to
system console

Aggregator
assembly

Silicone tubing, all
parylene coated

Module components,
2 places

Delivery optics and
connections to
cameras

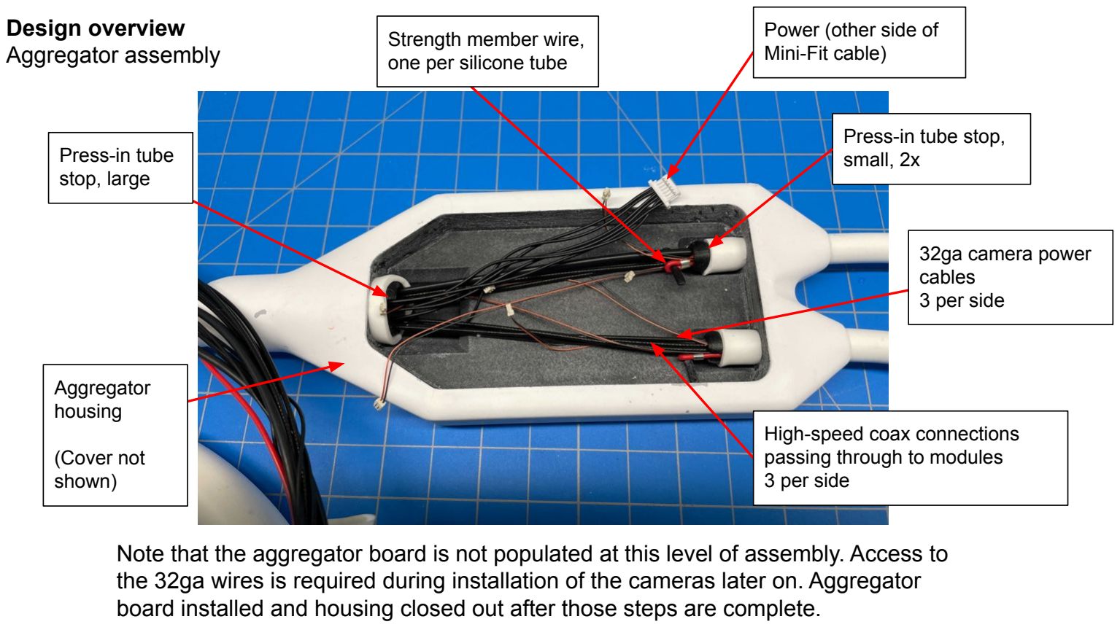
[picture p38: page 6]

Design overview
Aggregator assembly

Power (other side of
Mini-Fit cable)

High-speed coax connections passing through to modules 3 per side

32ga camera power
cables
3 per side

Note that the aggregator board is not populated at this level of assembly. Access to the 32ga wires is required during installation of the cameras later on. Aggregator board installed and housing closed out after those steps are complete.

Press-in tube
stop, large

Press-in tube stop,
small, 2x

Strength member wire,
one per silicone tube

Aggregator
housing

(Cover not
shown)

Design overview
Module connections and delivery optics

32ga camera
power cable,
3x

High-speed
coax, 3x

Micro SMA

Laser tip assembly

Module components, 2 places

Diffuser
+
window

Clamshell
housing Fiber and
ferrule

Spring

The fiber is tacked in place during assembly with UV cure adhesive

The laser tip assembly is potted with RTV after assembly

Injection holes

Spacer

Design overview
Connections to system console

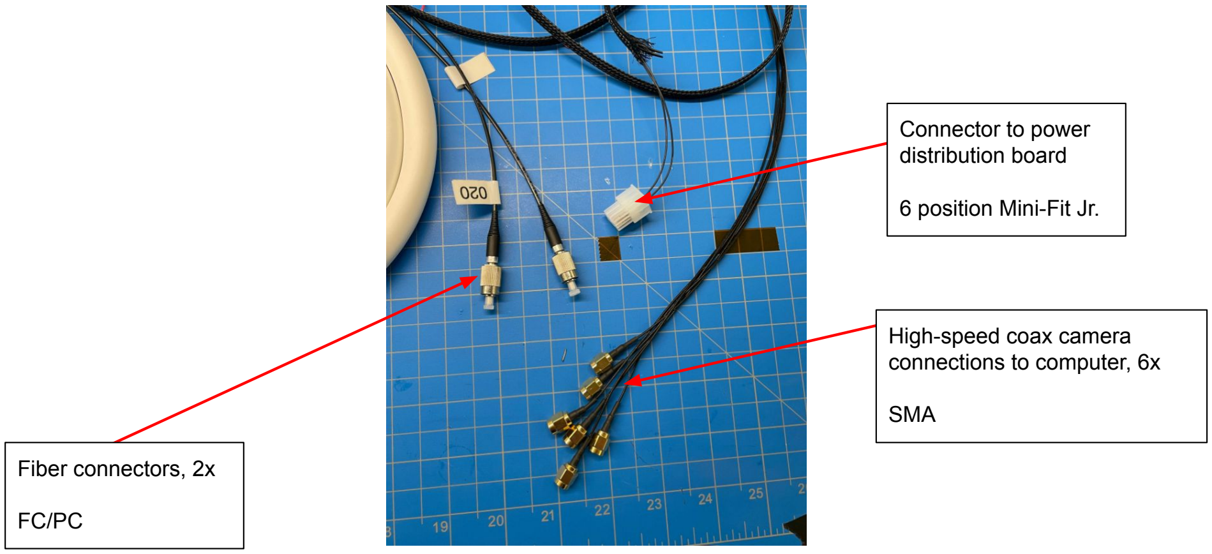
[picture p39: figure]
Fiber connectors, 2x; Connector to power distribution board; 6 position Mini-Fit Jr.; High-speed coax camera connections to computer, 6x; SMA

# Assembly process

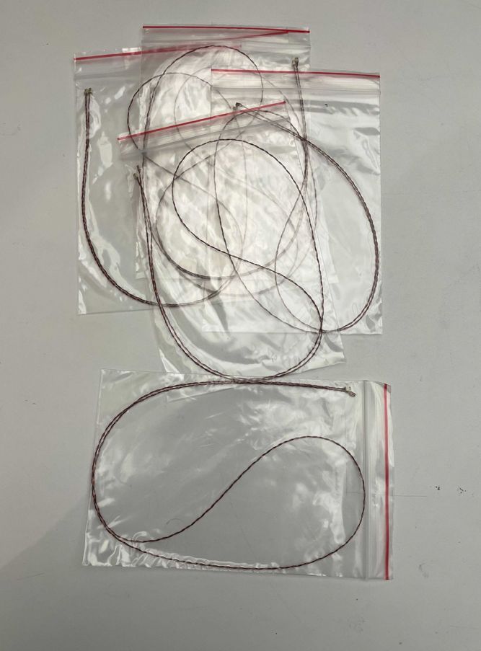
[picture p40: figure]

Obtain materials

32ga camera power cables
7000-xxxx
QTY 6

Note that these cables are twisted pairs, with dot of adhesive at rear of connector to act as strain relief

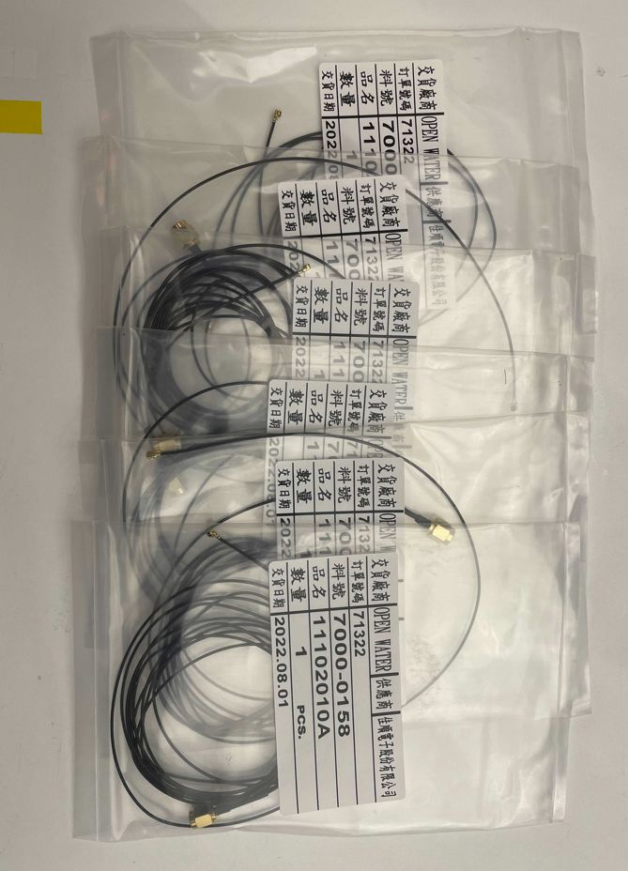
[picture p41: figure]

Obtain materials

High-speed coax camera cables 7000-0158
QTY 6

Obtain materials

6-wire power cable
7000-xxxx
QTY 1

Note that this part number will be updated with pre-installed Mini-Fit Jr. version

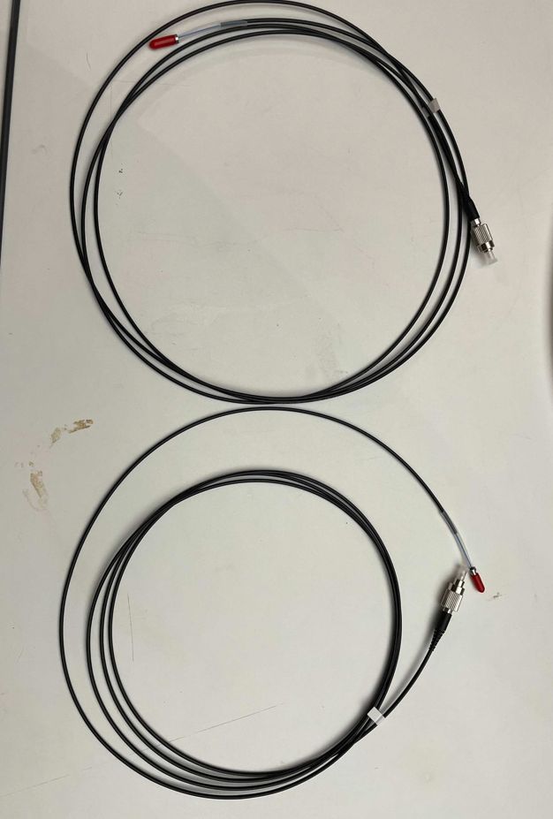
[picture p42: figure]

Make subassembly

Fiber assembly
7000-0141
QTY 2

Ensure that fibers are tagged with serial numbers near the fc/pc connectors, serial numbers are recorded, and fiber assembly transmission is tested

*Confirm adhesive curing process with pull test data recorded.

Obtain materials

Aggregator housing

1x Body
3000-xxxx

1x Lid
3000-xxxx

Prepare silicone tubing
Obtain parylene coated silicone tubing, large and small.

Cut to length with a razor blade. Ensure that both ends have been cut square.

2x (small tube, PN)
1x (large tube, PN)

Obtain materials

Sheath stop, large
3000-xxxx
QTY 1

Sheath stop, small
3000-xxxx
QTY 2

Glued to ~2m long flexible rod

large pull tool
3000-xxxx

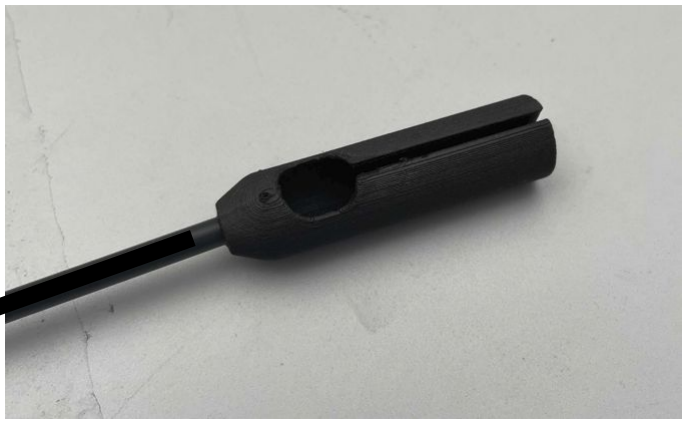
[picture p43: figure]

Cable and fiber ends will be fed into this tube, taped into place, and pulled through the large silicone tube

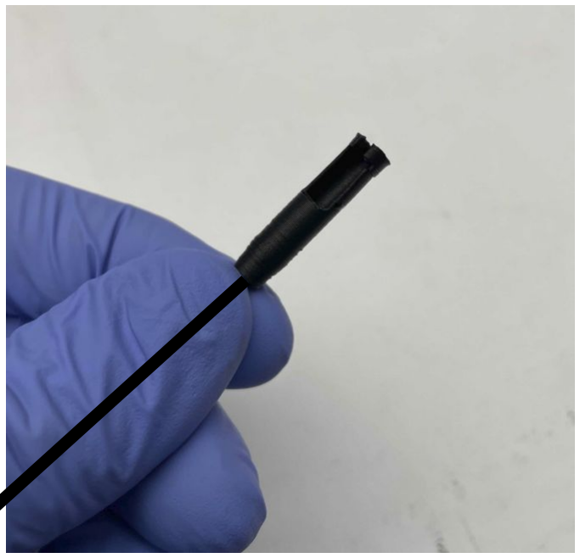
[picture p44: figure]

Glued to ~1m long heavy gauge flexible wire

small pull tool
3000-xxxx

Cable and fiber ends will be fed into this tube, taped into place, and pulled through the large silicone tube

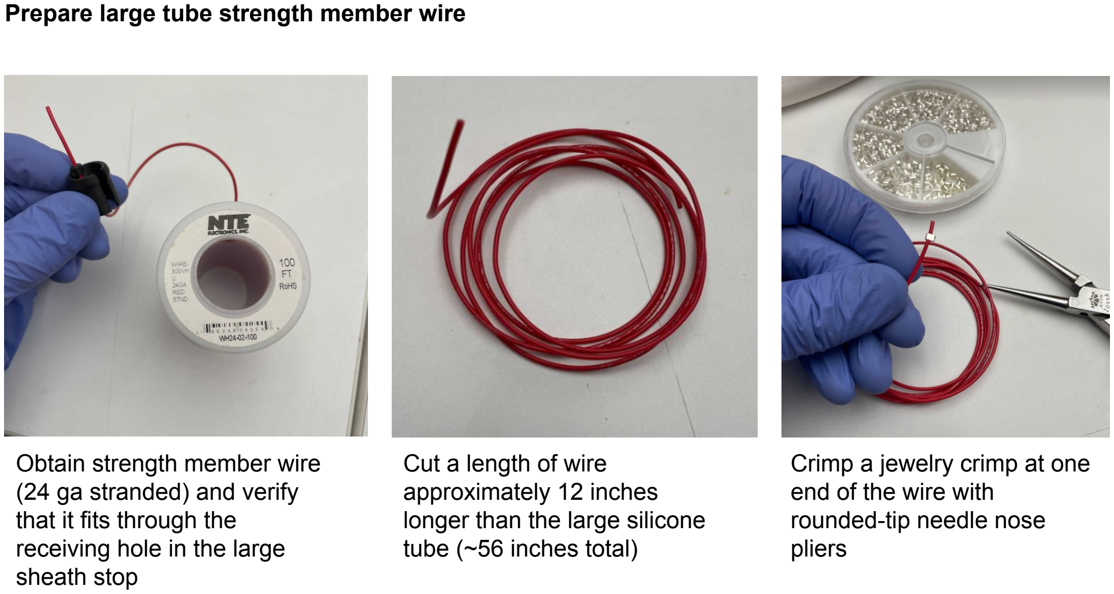
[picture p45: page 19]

Prepare large tube strength member wire

Obtain strength member wire (24 ga stranded) and verify that it fits through the
receiving hole in the large sheath stop

Cut a length of wire
approximately 12 inches
longer than the large silicone tube (~56 inches total)

Crimp a jewelry crimp at one end of the wire with
rounded-tip needle nose
pliers

Arrange cables to be pulled through silicone tube

Gather the component cables on the bench to be pulled through the large silicone tube
- 1x 6-wire power cable
- 6x high-speed coax able, micro SMA connectors at end ‘A’
- 2x fibers, ferrules at end ‘A’
- Strength member wire, crimped end at end ‘A’
It has been helpful for us to route them through a hook at the end of the table, and hold the bundle in place with a piece of Kapton tape

### End ‘A’

### End ‘B’

Load components into large pull tool

Load component cable/fiber ends into tool in this order:
1. 6-wire power cable
2. Fiber ferrules (with protective covers temporarily removed)
3. Micro-SMA coax cables
4. Strength member wire (crimped end)
Gather the wires to minimize the cross-section, and secure in place by wrapping a piece of tape around the tool (1-inch 3M Black ShurTape)

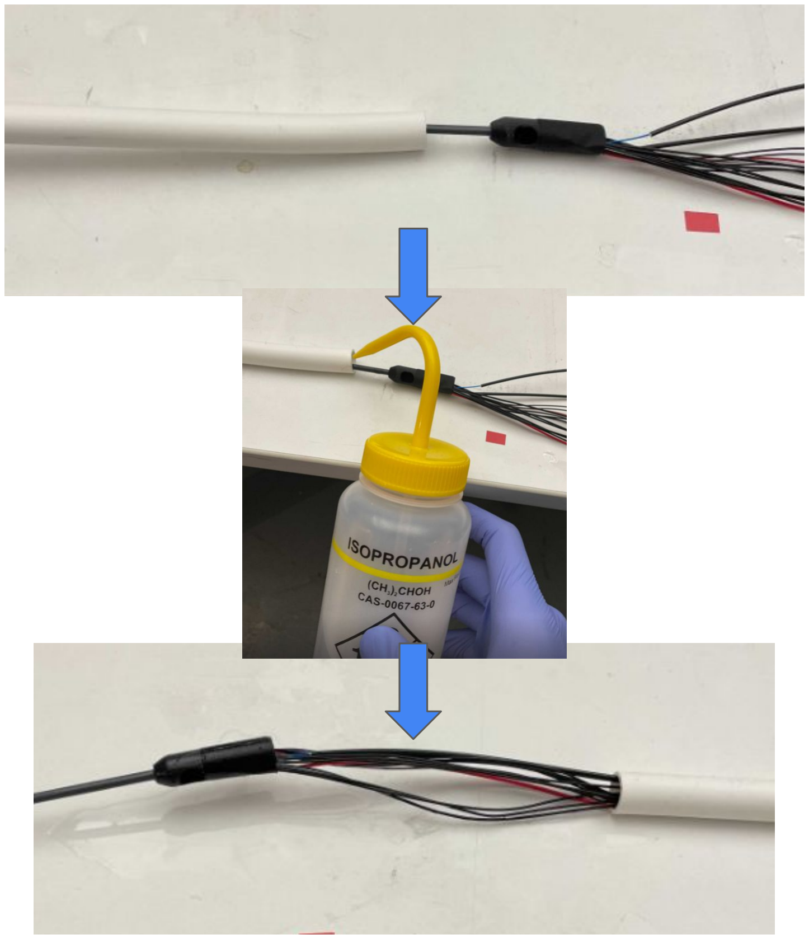
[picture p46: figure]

Pull components through large silicone tube

Slip the large silicone tube over the pull tool shaft, until it is close to the bundled cables as shown

Lubricate the tube by squirting in a small amount of IPA

Hold the end of the silicone tubing in place, and pull the tool through until the wires emerge from the other end

Wipe away excess alcohol, and replace the protective fiber ferrule caps

Feed the silicone tube and cables through the body of the aggregator housing as shown

Be careful not to pull the strength member or any cables completely into the tube

Tape End ‘B’ of the strength member end can be taped to the tube to prevent losing it

Feed large tube and cables through aggregator housing body

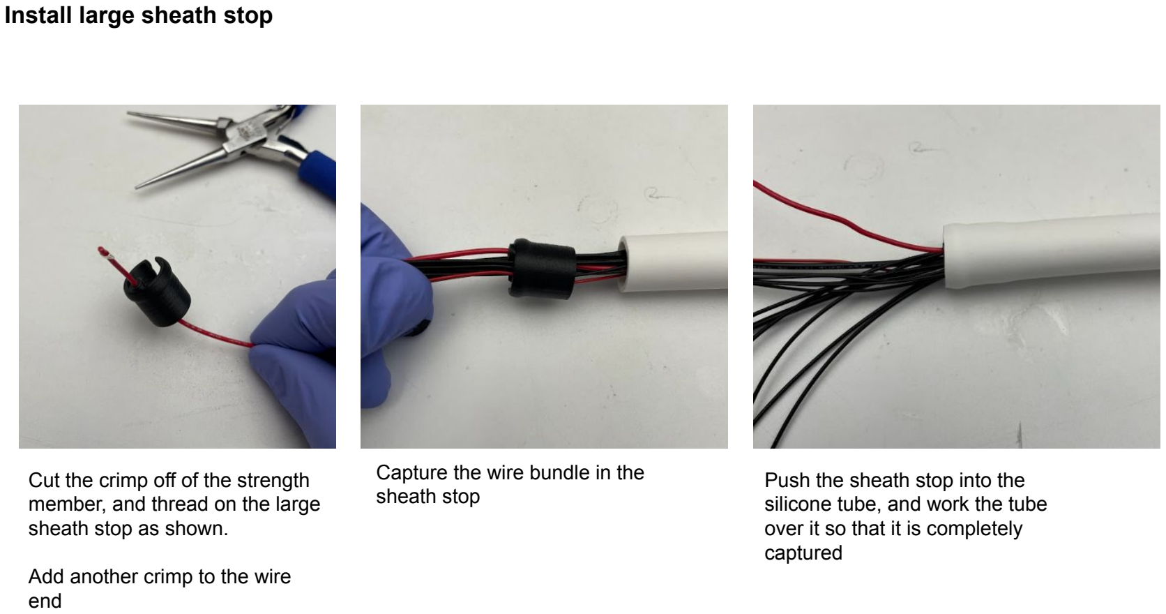
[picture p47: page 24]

Install large sheath stop

Cut the crimp off of the strength member, and thread on the large sheath stop as shown.

Add another crimp to the wire end

Capture the wire bundle in the sheath stop

Push the sheath stop into the silicone tube, and work the tube over it so that it is completely captured

Secure large tube and sheath stop in aggregator housing body

Pull

Slide the aggregator housing body over the sheath stop and wire bundle

Pull on the silicone tube to fully seat the sheath stop at the bottom of the housing interior

Pull any slack out of the strength member at end ‘B’. This will seat the crimp against the sheath stop.

Pull

Pull

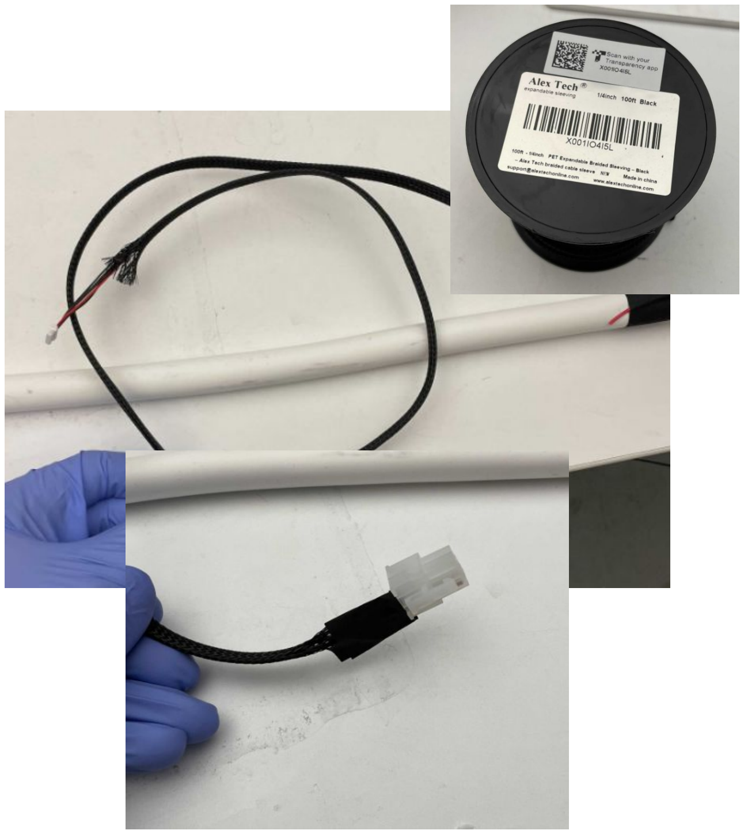
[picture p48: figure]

Wrap excess length of 6-wire power cable with ¼” braided sleeve material

Replace B end power connector with Mini-Fit Jr.

Note that this step will not be needed when we move to purpose-built Mini-Fit cables (we are currently reworking 6-wire cables we had on hand)

Prepare small tube strength members

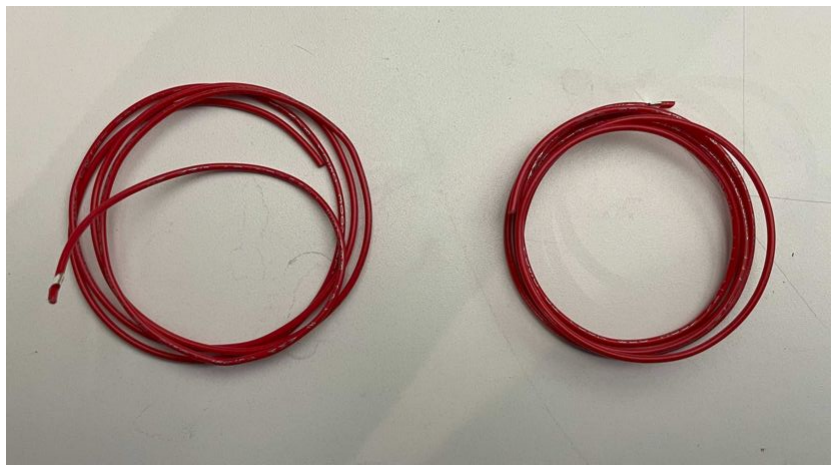
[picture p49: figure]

Cut two lengths of 24 AWG
stranded wire, ~30 inches long

Crimp a jewelry crimp at one end of each wire

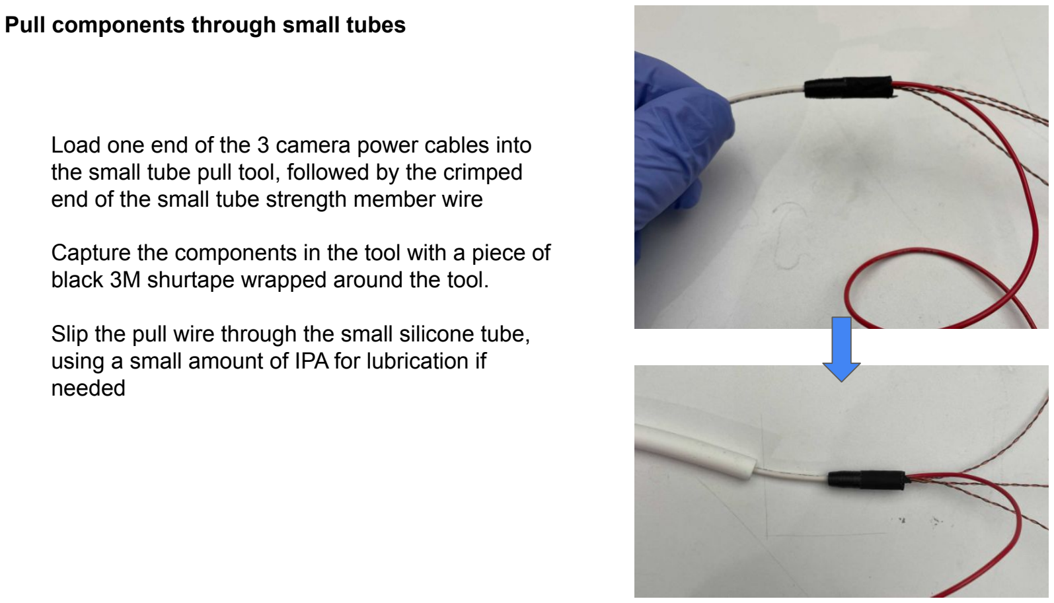
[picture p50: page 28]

Pull components through small tubes

Load one end of the 3 camera power cables into the small tube pull tool, followed by the crimped end of the small tube strength member wire

Capture the components in the tool with a piece of black 3M shurtape wrapped around the tool.

Slip the pull wire through the small silicone tube, using a small amount of IPA for lubrication if needed

Pull components through small tubes

Squirt a small amount of IPA into the tube, and carefully pull the assembly through the tube

Release the components from the tool and dry

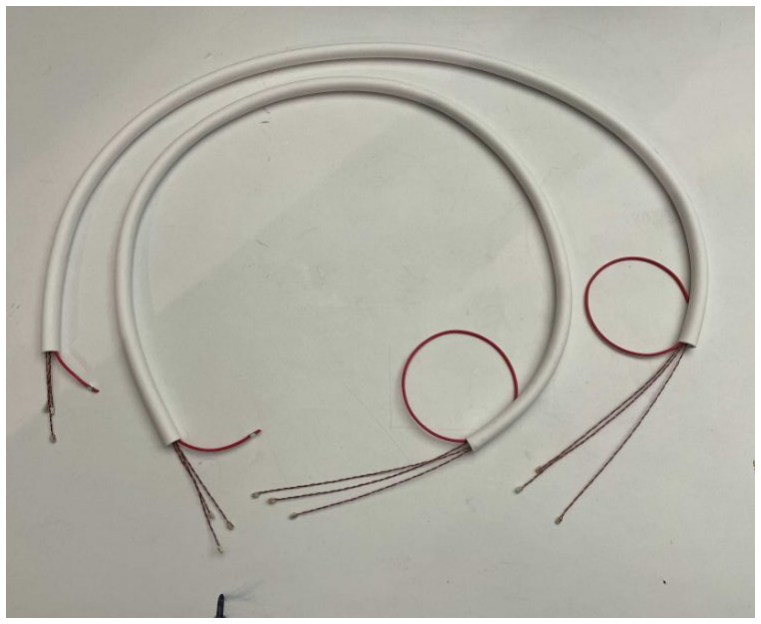
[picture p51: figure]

Repeat for second small tube assembly

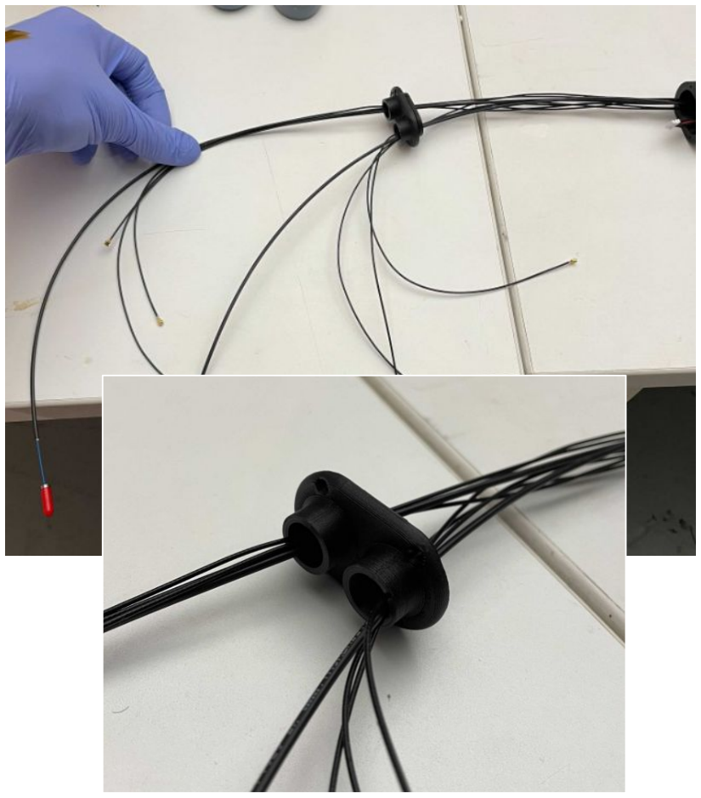
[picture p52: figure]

Guide wires through aggregator housing lid

Route the wires through the aggregator housing lid

Make sure that o-ring is installed on the lid, and that it is facing in the direction shown (o-ring side towards the aggregator housing body)

Route 3 micro-coax and one fiber through each port in the lid as shown

Push fibers and coax through small tubes

Position the small tube assembly on the bench in a straight line, secured with tape if needed, to help with passing wires.

Push through the fiber ferrule first (with safety cap removed), followed by the 3 micro coax cables.

Use a small amount of IPA for lubrication if needed.

Agg
housing Large tube

Push fibers and coax through small tubes

Repeat for second tube assembly

Replace the safety caps on the fiber ferrules

Agg
housing Large tube

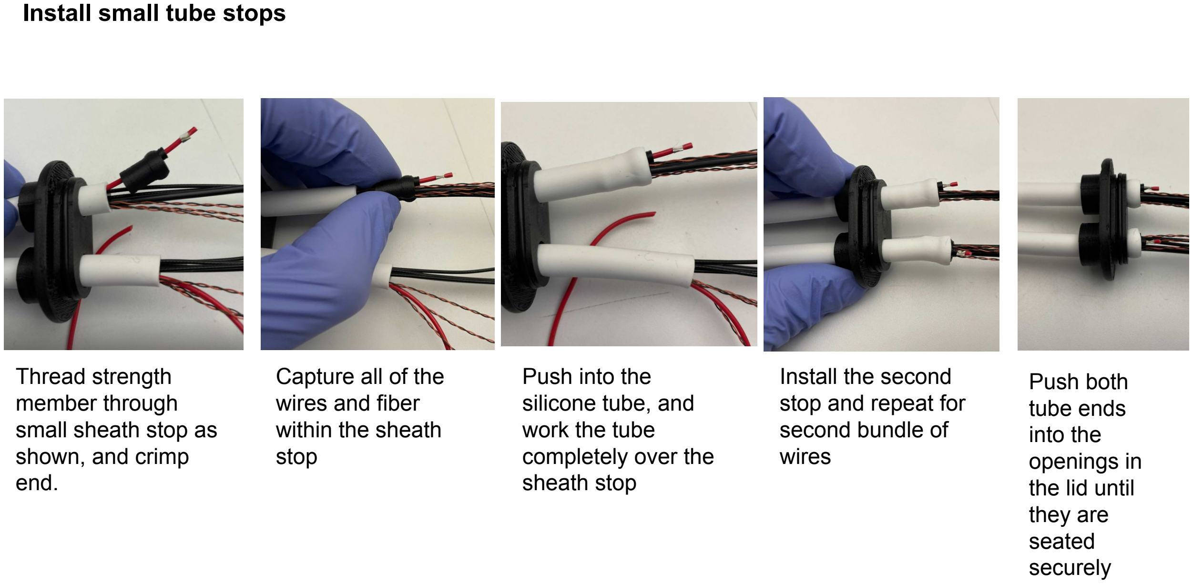
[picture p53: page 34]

Install small tube stops

Thread strength
member through
small sheath stop as
shown, and crimp
end.

Capture all of the
wires and fiber
within the sheath
stop

Push into the
silicone tube, and
work the tube
completely over the
sheath stop

Install the second
stop and repeat for
second bundle of
wires

Push both
tube ends
into the
openings in
the lid until
they are
seated
securely

Close up aggregator housing

Pull slack out of internal wires to bring the aggregator housing body and lid together.

Be careful to leave exposed length of the camera power wires and 6-wire cable so that they don’t get pulled into the tubes

Secure the lid to the body with 2 screws only (M2 x 10 mm). (this will be opened again later in system assembly)

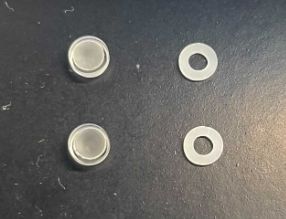
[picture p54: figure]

Obtain materials

Diffuser optic assemblies (previously assembled)
7000-0148
QTY 2

See 7400-0148 for assembly detail

Obtain materials

Fiber housing halves
3000-0480
3000-0481
2x each

Verify that housing halves snap together, then separate with tweezers

Spring
1000-xxxx
2x

Wind spring around black outer fiber sheath

Avoid blue tefzel section

Repeat for second fiber

Install ferrule backing spring

Fiber assembly tool

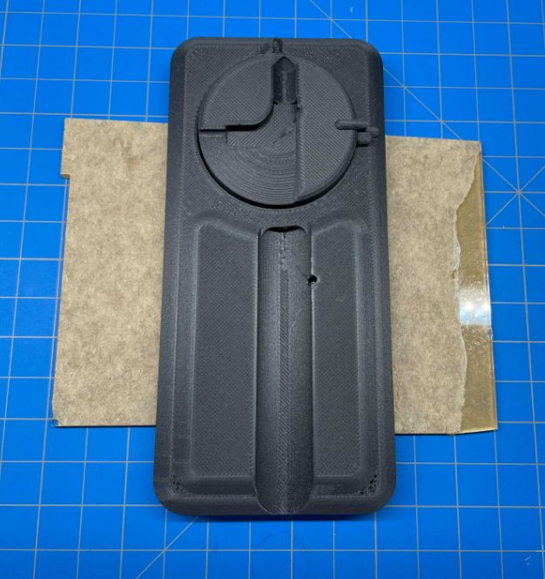
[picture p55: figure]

Obtain fiber assembly tool 7000-xxxx

Wipe clean prior to use

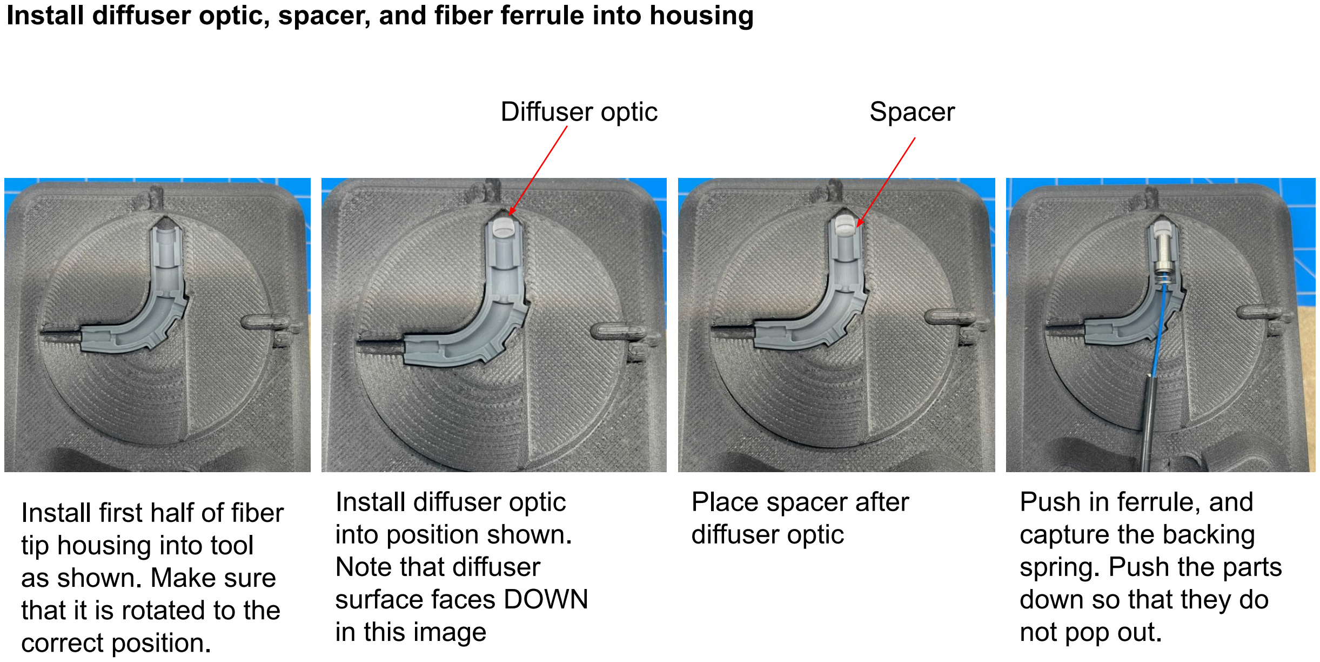
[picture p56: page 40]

Install diffuser optic, spacer, and fiber ferrule into housing

Install first half of fiber tip housing into tool
as shown. Make sure
that it is rotated to the
correct position.

Install diffuser optic
into position shown.
Note that diffuser
surface faces DOWN
in this image

Place spacer after
diffuser optic

Push in ferrule, and
capture the backing
spring. Push the parts
down so that they do
not pop out.
Diffuser optic | Spacer

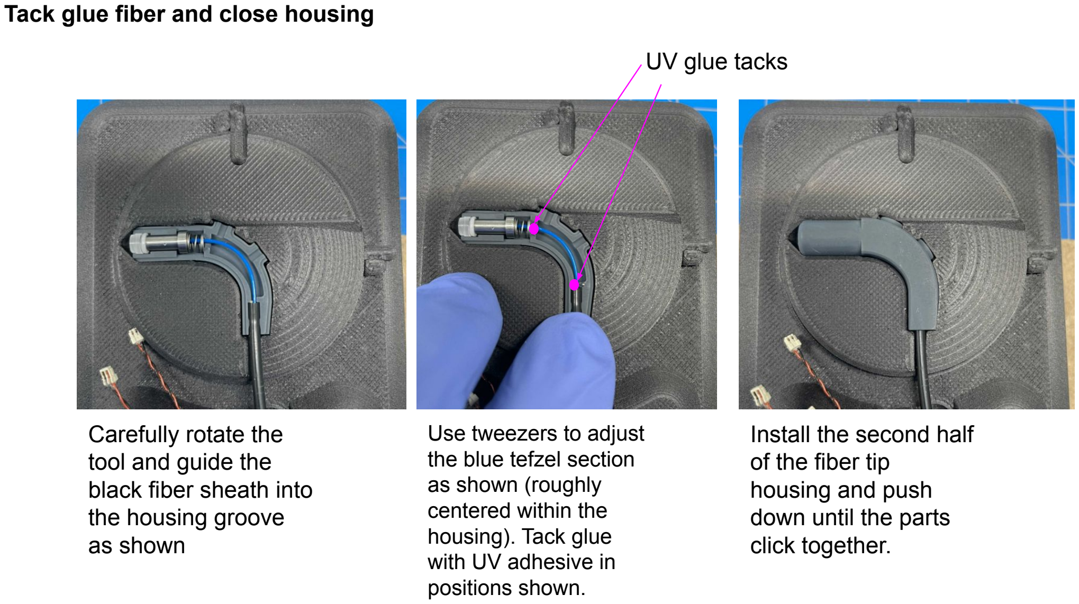
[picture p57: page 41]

Tack glue fiber and close housing

Carefully rotate the
tool and guide the
black fiber sheath into
the housing groove
as shown

Use tweezers to adjust
the blue tefzel section
as shown (roughly
centered within the
housing). Tack glue
with UV adhesive in
positions shown.

Install the second half
of the fiber tip
housing and push
down until the parts
click together.

UV glue tacks

Glue and pot fiber tip assembly

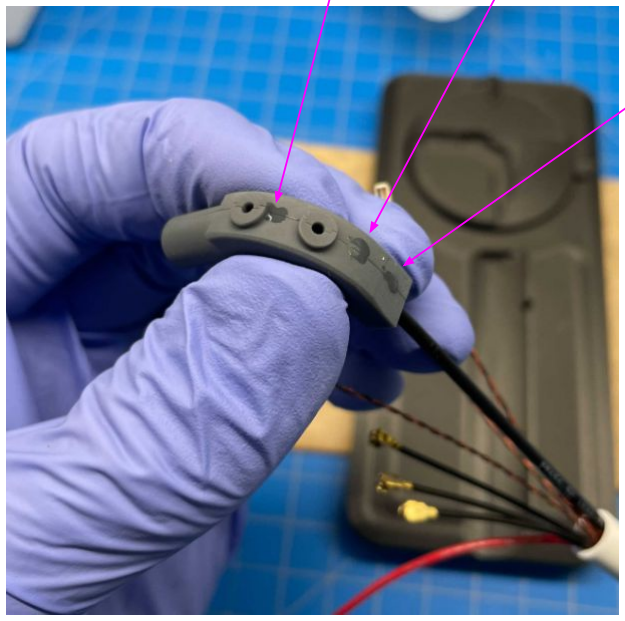
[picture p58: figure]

Carefully remove the fiber tip assembly from the tool, and tack glue with UV adhesive in positions shown

Glue and pot fiber tip assembly

Apply a generous amount of UV cure adhesive to the pocket where the black fiber sheath exits the tip assembly, and cure

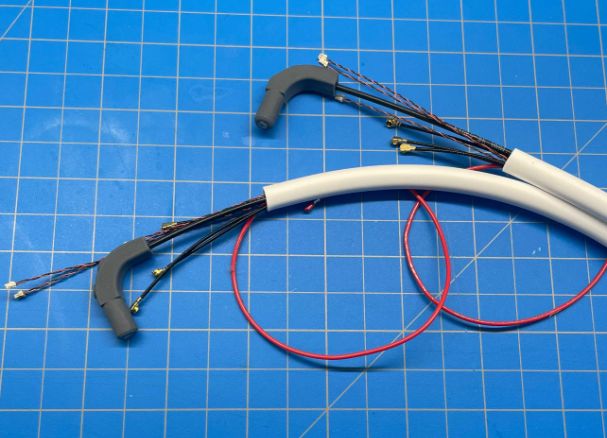
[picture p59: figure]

Repeat assembly and UV glueing steps for the second laser tip assembly.

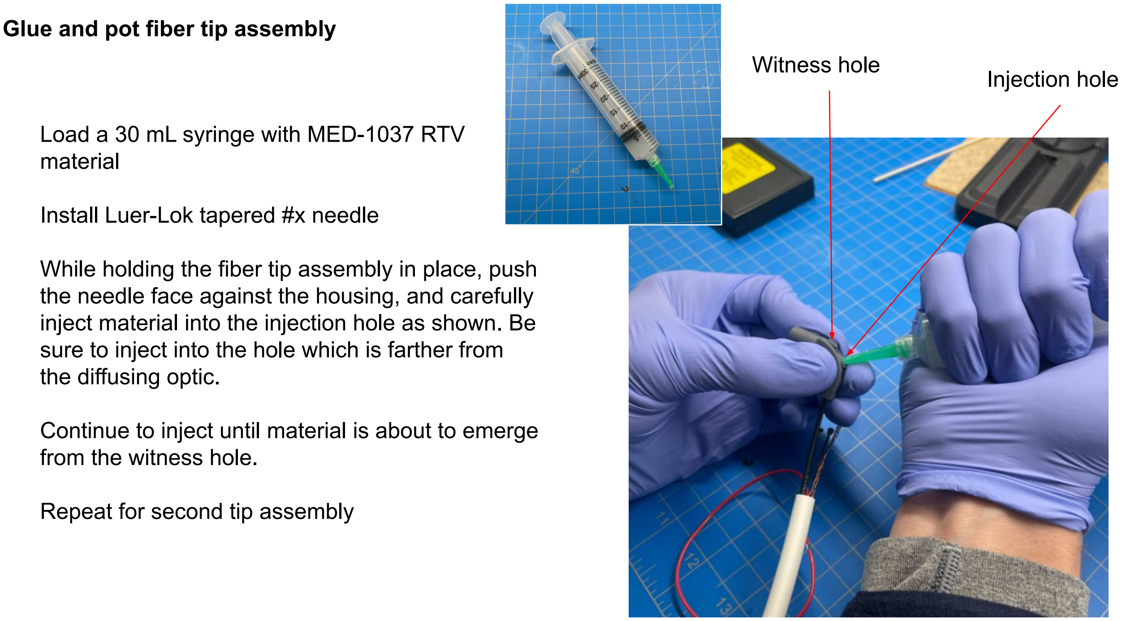
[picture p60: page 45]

Glue and pot fiber tip assembly

Load a 30 mL syringe with MED-1037 RTV material

Install Luer-Lok tapered #x needle

While holding the fiber tip assembly in place, push the needle face against the housing, and carefully inject material into the injection hole as shown. Be sure to inject into the hole which is farther from the diffusing optic.

Continue to inject until material is about to emerge from the witness hole.

Repeat for second tip assembly

Injection hole Witness hole

Seal aggregator housing tube exit points

Tube exits sealed

Replace the syringe tip with a #TBD

Carefully inject the RTV in the groove at the exit of each tube from the aggregator housing

Ensure that the grooves are filled to their full depth, and that there is sealing all around.

Wipe away any excess material.

Repeat process for each tube.

Note that full ambient temperature cure time for MED-1037 is approximately 72 hours.

Cable complete

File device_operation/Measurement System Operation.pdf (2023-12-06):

Measurement System Operation / Sequence of Events

1. Instrument Powered “On”
2. Power Distribution Unit sequences power to all peripherals
3. TDA4 RVP powers up/initialization
4. Touch Display power up initialization
5. Peripherals initialized
a. Laser Safety System
b. Laser Control System
c. FPDLink- Himax HM5530 Cameras (Through TDA4 RVP)
d. 1x8 Fiber Optic Switch

Completion of these steps constitutes “Measuremet System Ready”

Patient Measurements

1. Operator positions camera-laser headset on patient
2. “Measurement Check”
a. Trigger Laser and acquire frames from cameras 1 and 2, compute black level parameters and image histogram
b. Move 1 x8 Fiber Switch to alternate position
c. Trigger laser and acquire frames from camera 3 and 4,compute black level paramters and image histogram
d. Confirm correctly positioned headset
3. “Patient Measurement”
a. Move 1 x 8 Fiber Switch to first position
b. Trigger laser
c. Acquire frames from cameras 1 and 2
d. Compute black level image mean and variance
e. Compute image histogram
f. Store image histogram
g. Repeat n times
h. Move 1 x 8 Fiber Switch to second position
i. Trigger laser
j. Acquire frames from cameras 1 and 2
k. Compute black level image mean and variance
l. Compute image histogram
m. Store image histogram
n. Repeat n times
o. Repeat m times

After initialization, these activities are generally controlled through the touch interface on the instrument. Error reporting will be to this display and all user control functions are routed to this display Laser Safety Functions, Power Distribution Unit related functions and Laser Pulse height and width will be accessible through this interface but not by a normal end user

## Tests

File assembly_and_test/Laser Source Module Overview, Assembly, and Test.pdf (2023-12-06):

Laser Source Module Overview,

# Assembly, and Test

## Overview

- Class 4 785 nm fiber coupled laser source assembly
- Consists of several optical components and printed circuit assemblies

attached to an aluminum baseplate

- Approximate size: 255 x 205 x 40 mm, 1.5 kg

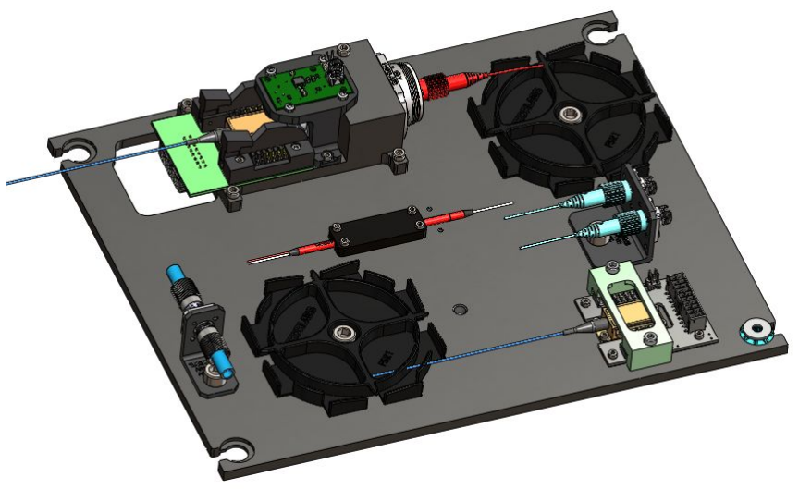
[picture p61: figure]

## Summary of Manufacturing Tests

Test | Rationale
Seed output power | Basic performance check, helpful for troubleshooting
TA output energy before isolator | Easy check during assembly, helpful for troubleshooting
Output energy after free space isolator alignment | Required for alignment
Output energy after fiber port alignment (both channels) | Required for alignment Output of both channels is critical
Beam profile | Characterize laser component performance.

Not required if already performed by supplier. Beam trace on oscilloscope

Speckle contrast

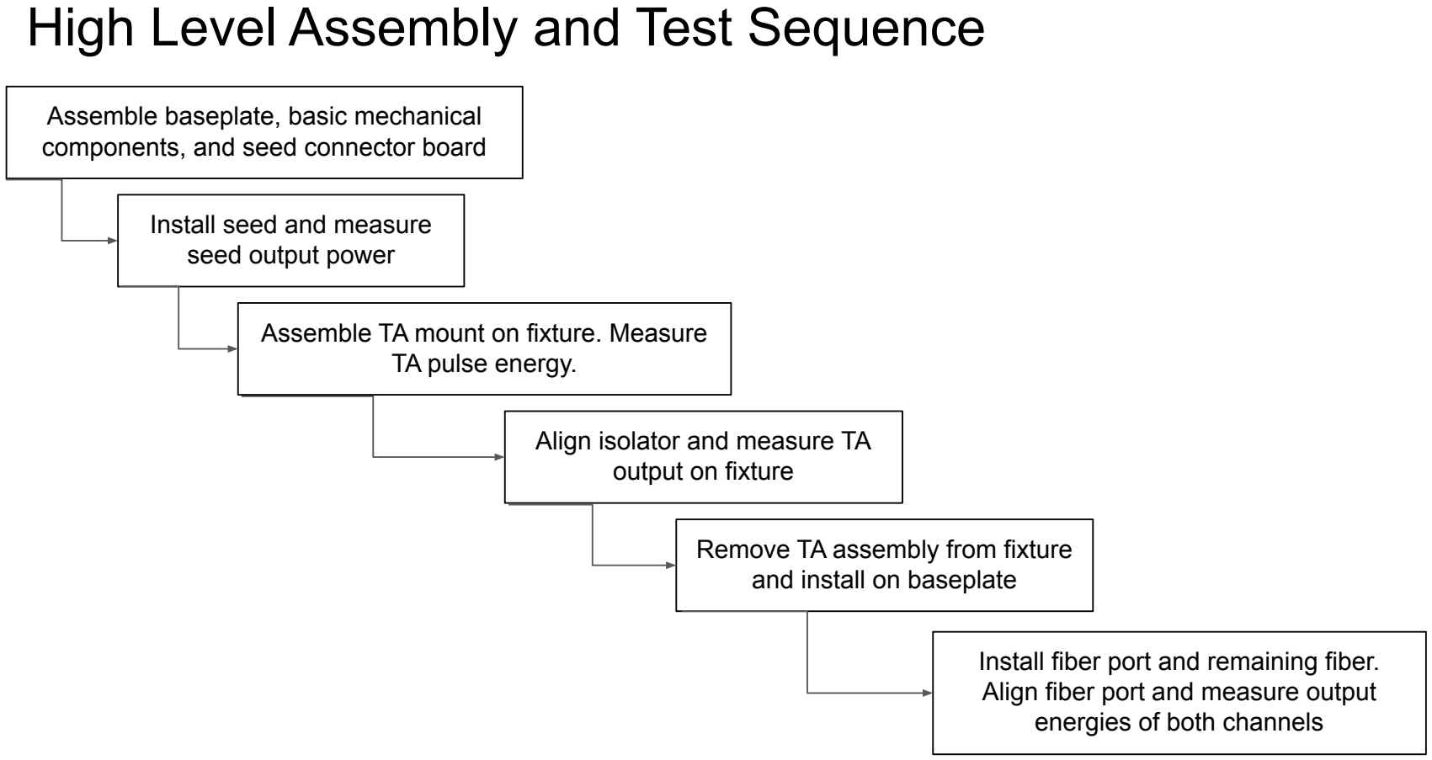
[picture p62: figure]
High Level Assembly and Test Sequence; Assemble baseplate, basic mechanical components, and seed connector board; Install seed and measure seed output power; Assemble TA mount on fixture. Measure TA pulse energy.; Remove TA assembly from fixture and install on baseplate; Align isolator and measure TA output on fixture; Install fiber port and remaining fiber. Align fiber port and measure output energies of both channels

## Assembly and Test Sequence

## Safety and Handling Precautions

- Seed and TA are both Class 4 laser products
- Seed and TA are both ESD sensitive, damage thresholds below 125 V
- Several sensitive optical surfaces including TA output window, isolator optics,

and fiber port optic

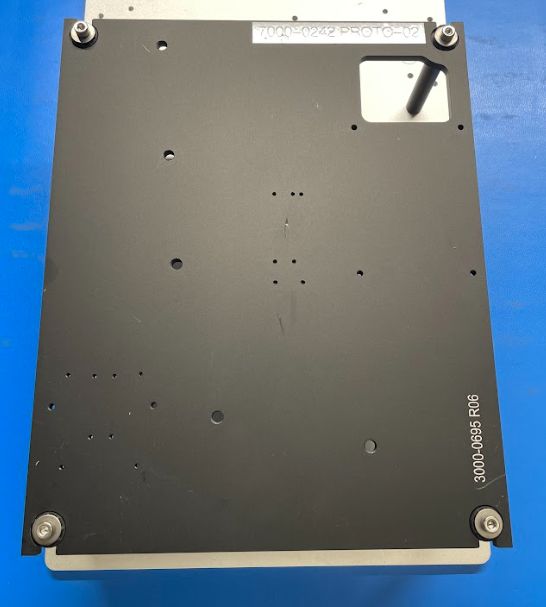
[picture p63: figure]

Install baseplate onto
holding fixture

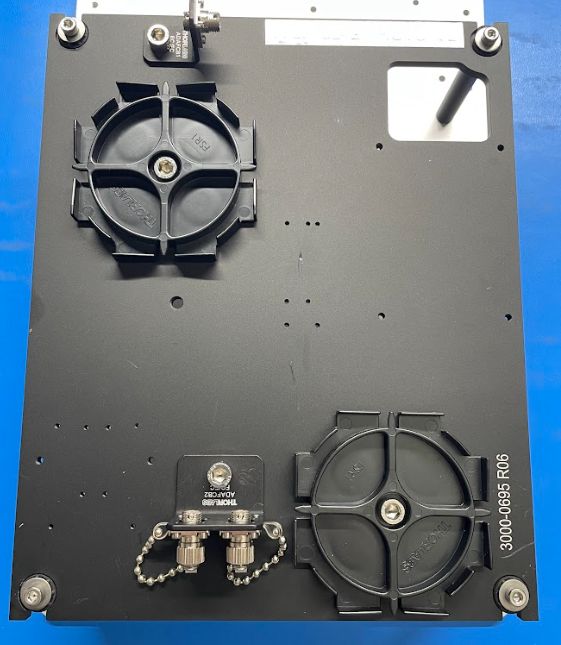
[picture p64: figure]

Install

2x fiber trays

1x ADAFCB3 (caps on)

1x ADAFCB1 (caps off)

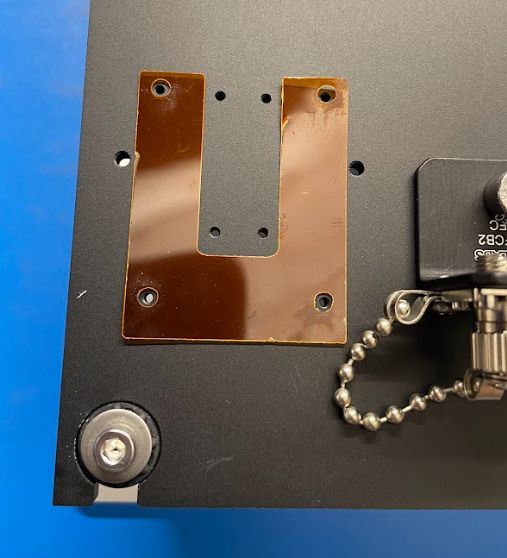
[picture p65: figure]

Lay down seed kapton shim
in position shown

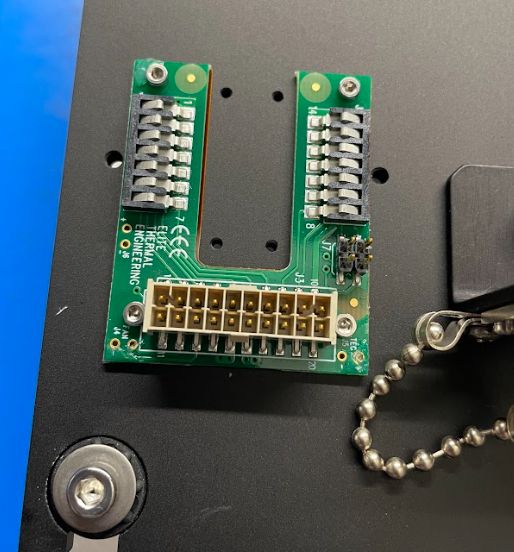
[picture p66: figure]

Install seed connector board on top of insulating shim

Secure with 4x m2x6 screws

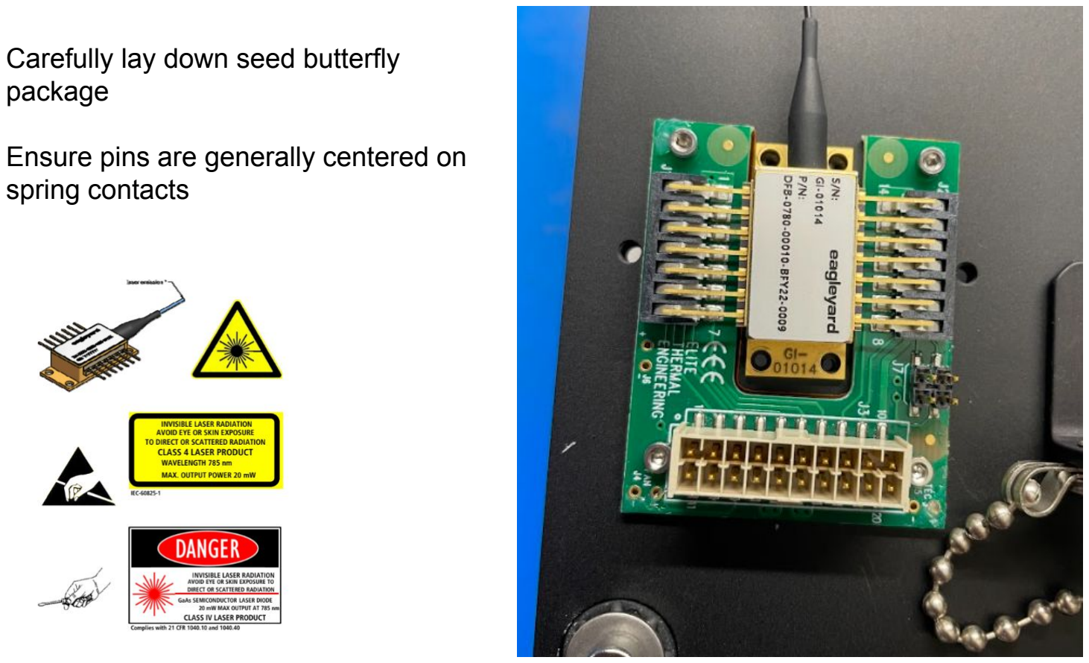
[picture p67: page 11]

Carefully lay down seed butterfly package

Ensure pins are generally centered on spring contacts

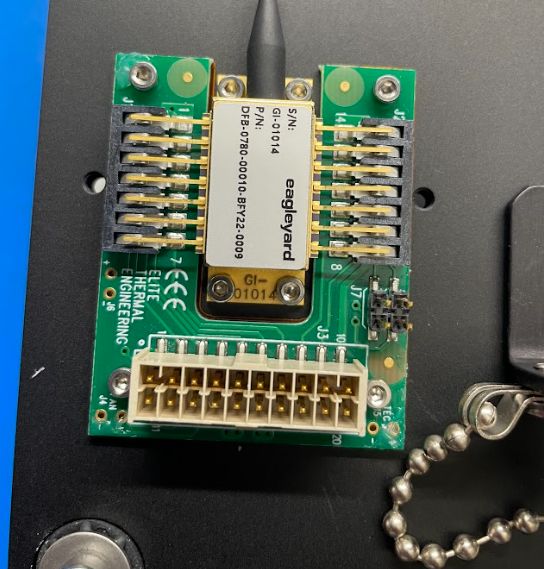
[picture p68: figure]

Carefully install and torque 4x m2x6 screws to secure
seed package

Ensure that pins stay
centered on spring contacts as well as possible during screw installation

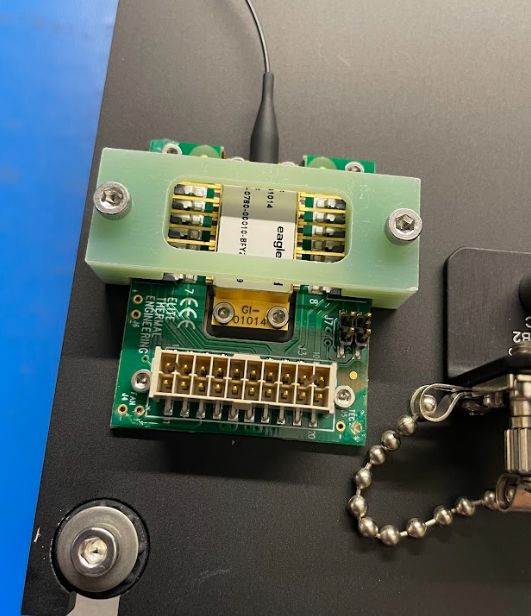
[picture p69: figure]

Install G10 clamp and
carefully secure with 2 m3 screws, alternating back and forth and incrementally
torqueing them down

Wrap seed fiber around tray

Carefully mate APC
connector to mating sleeve

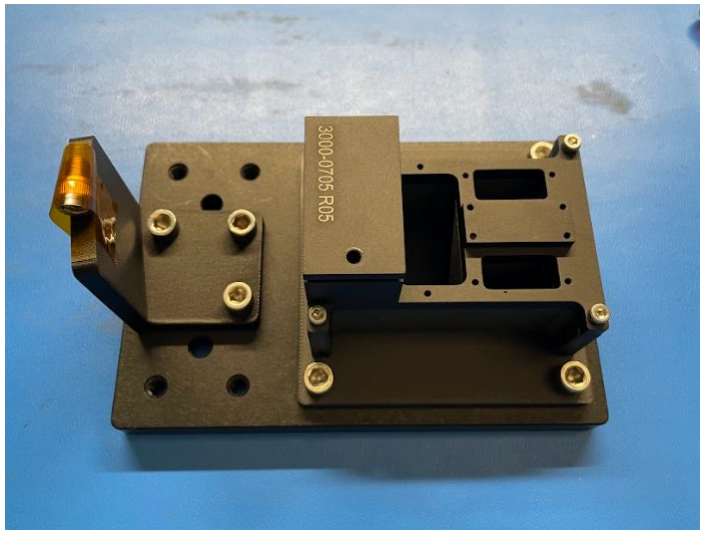
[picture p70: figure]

Install TA mount onto TA
assembly and test fixture
with 4x m3x8 screws


Lay down TA kapton shim in position shown


Install TA connector board on top of insulating shim

Secure with 4x m2x12 screws


Carefully lay down TA
butterfly package

Ensure that pins are
correctly positioned on
connector, and that
attachment screw holes are approximately aligned


Carefully secure the
butterfly package with 4x
m2x6 screws, carefully
bringing up the torque on
each one

Stay aware of any gaps
below the butterfly package and avoid forcing large
movements or causing pin
bending when torqueing
screws

Avoid any contact to the TA output window


Snap the two ZIF connector arms closed. They should
snap firmly, without rattling or overly straining the
components

Note that the orientation of the ZIF connector is
backwards in this image -
the angled arms should be
on the same side of the
board as the exiting fiber


Install the ophir sensor to the assembly and measure
TA output energy


Carefully install the free space isolator as shown

Note the orientation of the isolator - the small stepped section should face the TA

Avoid contacting the isolator optical windows. Also note that the isolator contains a magnet, and is prone to
attracting screws and tools


Install isolator locating tool with 3x 2-56 screws

Install m3 isolator flexure adjustment screw. Screw in until it just touches the surface of the flexure arm


Perform isolator alignment, rotating manually to
maximize output. See
detailed procedure

Keep the isolator seated
against the positioning tool

Torque the flexure
adjustment screw until the isolator can no longer rotate


Remove the isolator locating tool

Install the fiber port with 3x 2-56 screws


Transfer the TA assembly to the baseplate and secure
with 4x m3 screws

Wrap excess TA fiber
around fiber tray and mate to APC sleeve

Perform fiber port alignment process


Clamp down the body of the 50:50 splitter in location shown

Use a dab of RTV in the
clamp groove

Note the orientation of the splitter - the two 50:50 arms exit upwards in this view

Tape down any stray fiber
length with kapton tape


Wrap the two splitter output fibers around the other fiber tray

Mate the FC/PC connectors
to the two output channel
sleeves as shown

Secure any loose fiber with kapton tape

Perform energy
measurements for both
output channels

Perform output channel energy measurements


Install PEEK photodiode board holder with 4x m2 screws.

Install photodiode board and secure with adhesive

Install photodiode cover with 4x m3 screws

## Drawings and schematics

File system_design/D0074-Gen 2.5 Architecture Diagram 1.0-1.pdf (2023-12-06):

# TA PWR

# Gen 2.5 Electrical Architecture TDA4Vx-16 Ch

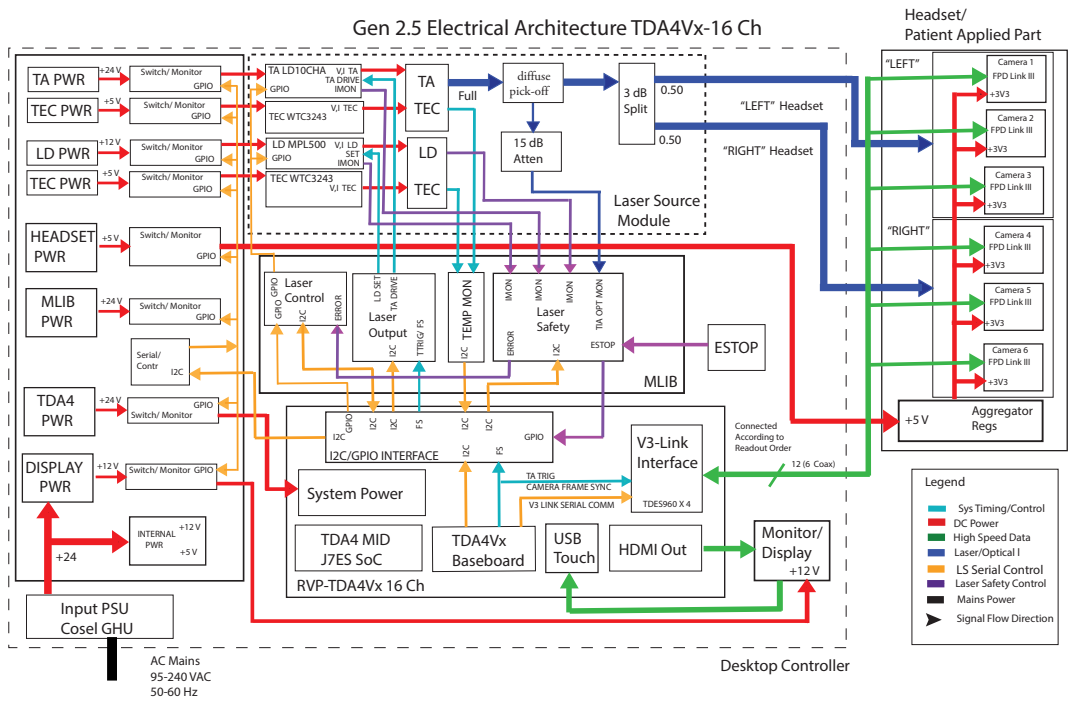
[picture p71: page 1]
Desktop Controller; TDA4Vx Baseboard; Input PSU Cosel GHU; TDA4 MID J7ES SoC; V3-Link Interface; AC Mains 95-240 VAC 50-60 Hz; Legend; RVP-TDA4Vx 16 Ch; TA LD10CHA; LD MPL500; Serial/ Contr; System Power; HDMI Out; Monitor/ Display; Laser Source Module; TEC WTC3243; TEC PWR; LD PWR; Switch/ Monitor; TEC; TDA4; PWR; DISPLAY PWR; HEADSET PWR; MLIB PWR; INTERNAL PWR; diffuse pick-off; 15 dB Atten; 3 dB Split; Laser Safety; TEMP MON; Laser Output; GPIO; Laser Control; I2C/GPIO INTERFACE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

Headset/
Patient Applied Part

TIA OPT MON

TTRIG/ FS FS

TA TRIG
CAMERA FRAME SYNC
V3 LINK SERIAL COMM
USB
Touch

Sys Timing/Control
DC Power
High Speed Data
ISO
PDU
Reg
LS Serial Control
Laser Safety Control
Mains Power
Signal Flow Direction

# TA PWR

TA

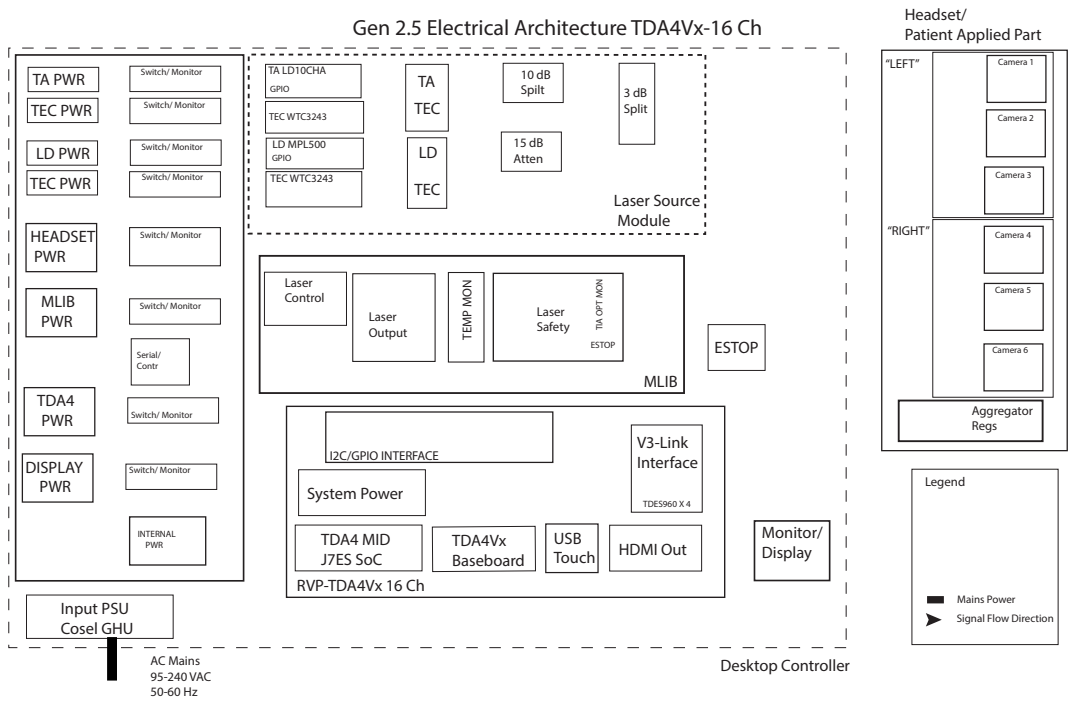
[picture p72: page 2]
TDA4Vx Baseboard; Input PSU Cosel GHU; TDA4 MID J7ES SoC; V3-Link Interface; AC Mains; Legend; RVP-TDA4Vx 16 Ch; TA LD10CHA; LD MPL500; Serial/ Contr; System Power; HDMI Out; Monitor/ Display; Laser Source Module; TEC WTC3243; TEC PWR; LD PWR; Switch/ Monitor; TEC; TDA4; PWR; DISPLAY PWR; HEADSET PWR; MLIB PWR; INTERNAL PWR; 10 dB Spilt; 15 dB Atten; 3 dB Split; Laser Safety; TEMP MON; Laser Output; GPIO; Laser Control; I2C/GPIO INTERFACE; TDES960 X 4; ESTOP; Aggregator Regs; Camera 1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

TIA OPT MON

TTRIG/ FS FS

TA TRIG
CAMERA FRAME SYNC
V3 LINK SERIAL COMM
USB
Touch

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

# TA PWR

TA

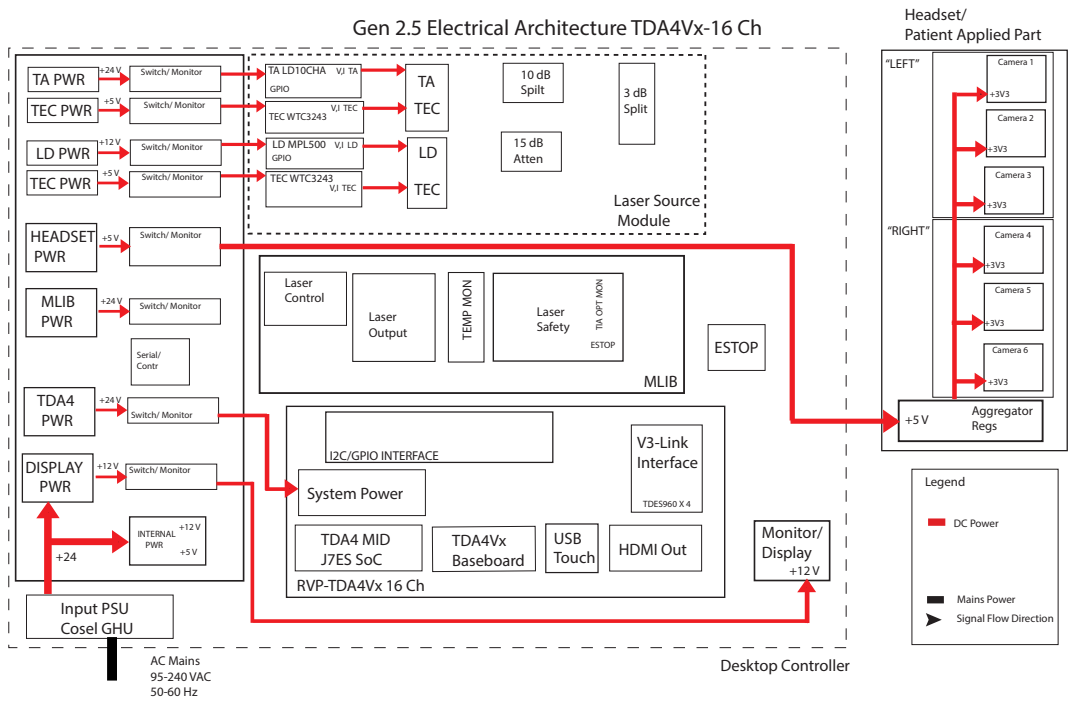
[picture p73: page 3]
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

TIA OPT MON

TTRIG/ FS FS

TA TRIG
CAMERA FRAME SYNC
V3 LINK SERIAL COMM
USB
Touch

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

# TA PWR

TA

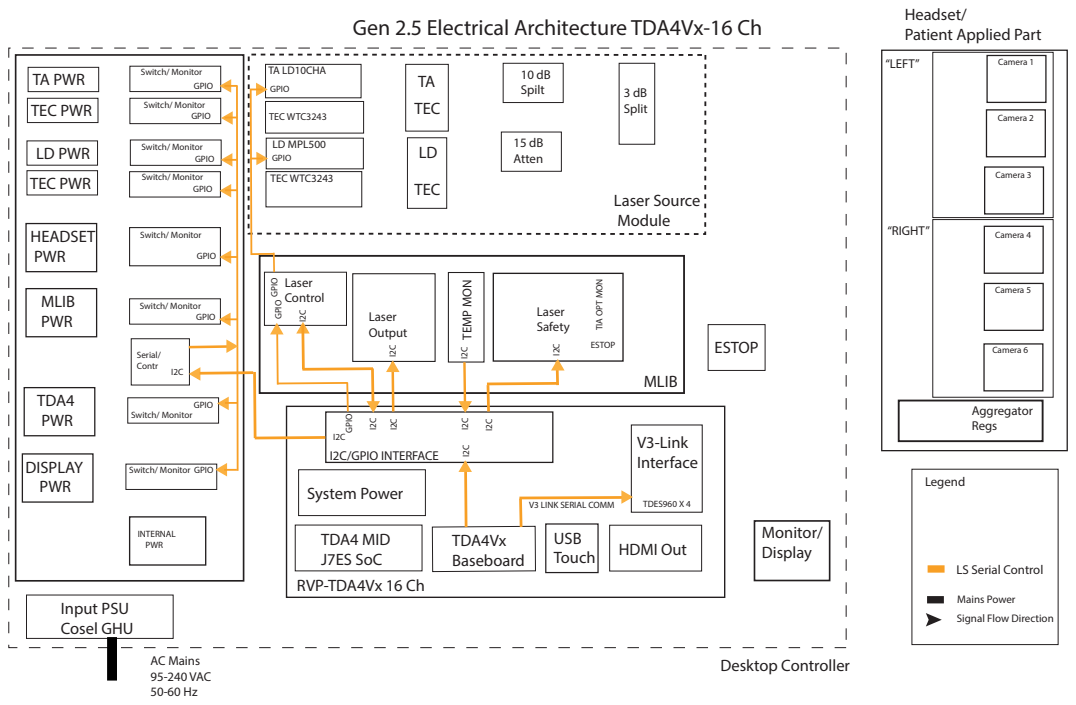
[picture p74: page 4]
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

TIA OPT MON

TTRIG/ FS FS

TA TRIG
CAMERA FRAME SYNC
V3 LINK SERIAL COMM
USB
Touch

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

# TA PWR

TA

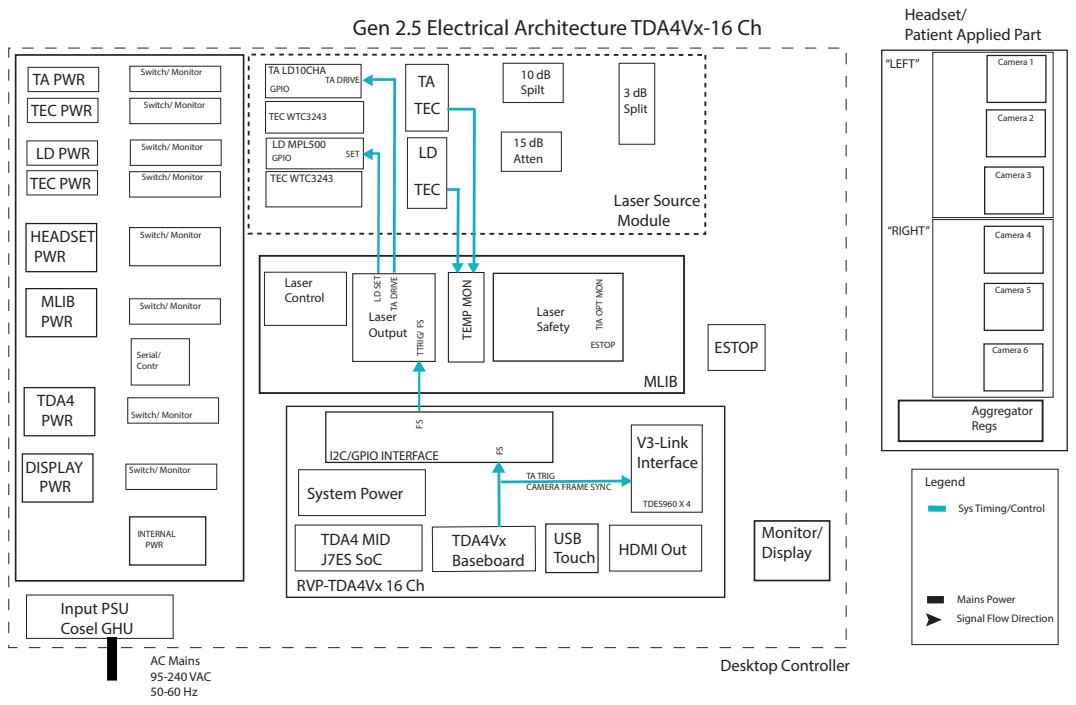
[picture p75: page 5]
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

TIA OPT MON

TTRIG/ FS FS

TA TRIG
CAMERA FRAME SYNC
V3 LINK SERIAL COMM
USB
Touch

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

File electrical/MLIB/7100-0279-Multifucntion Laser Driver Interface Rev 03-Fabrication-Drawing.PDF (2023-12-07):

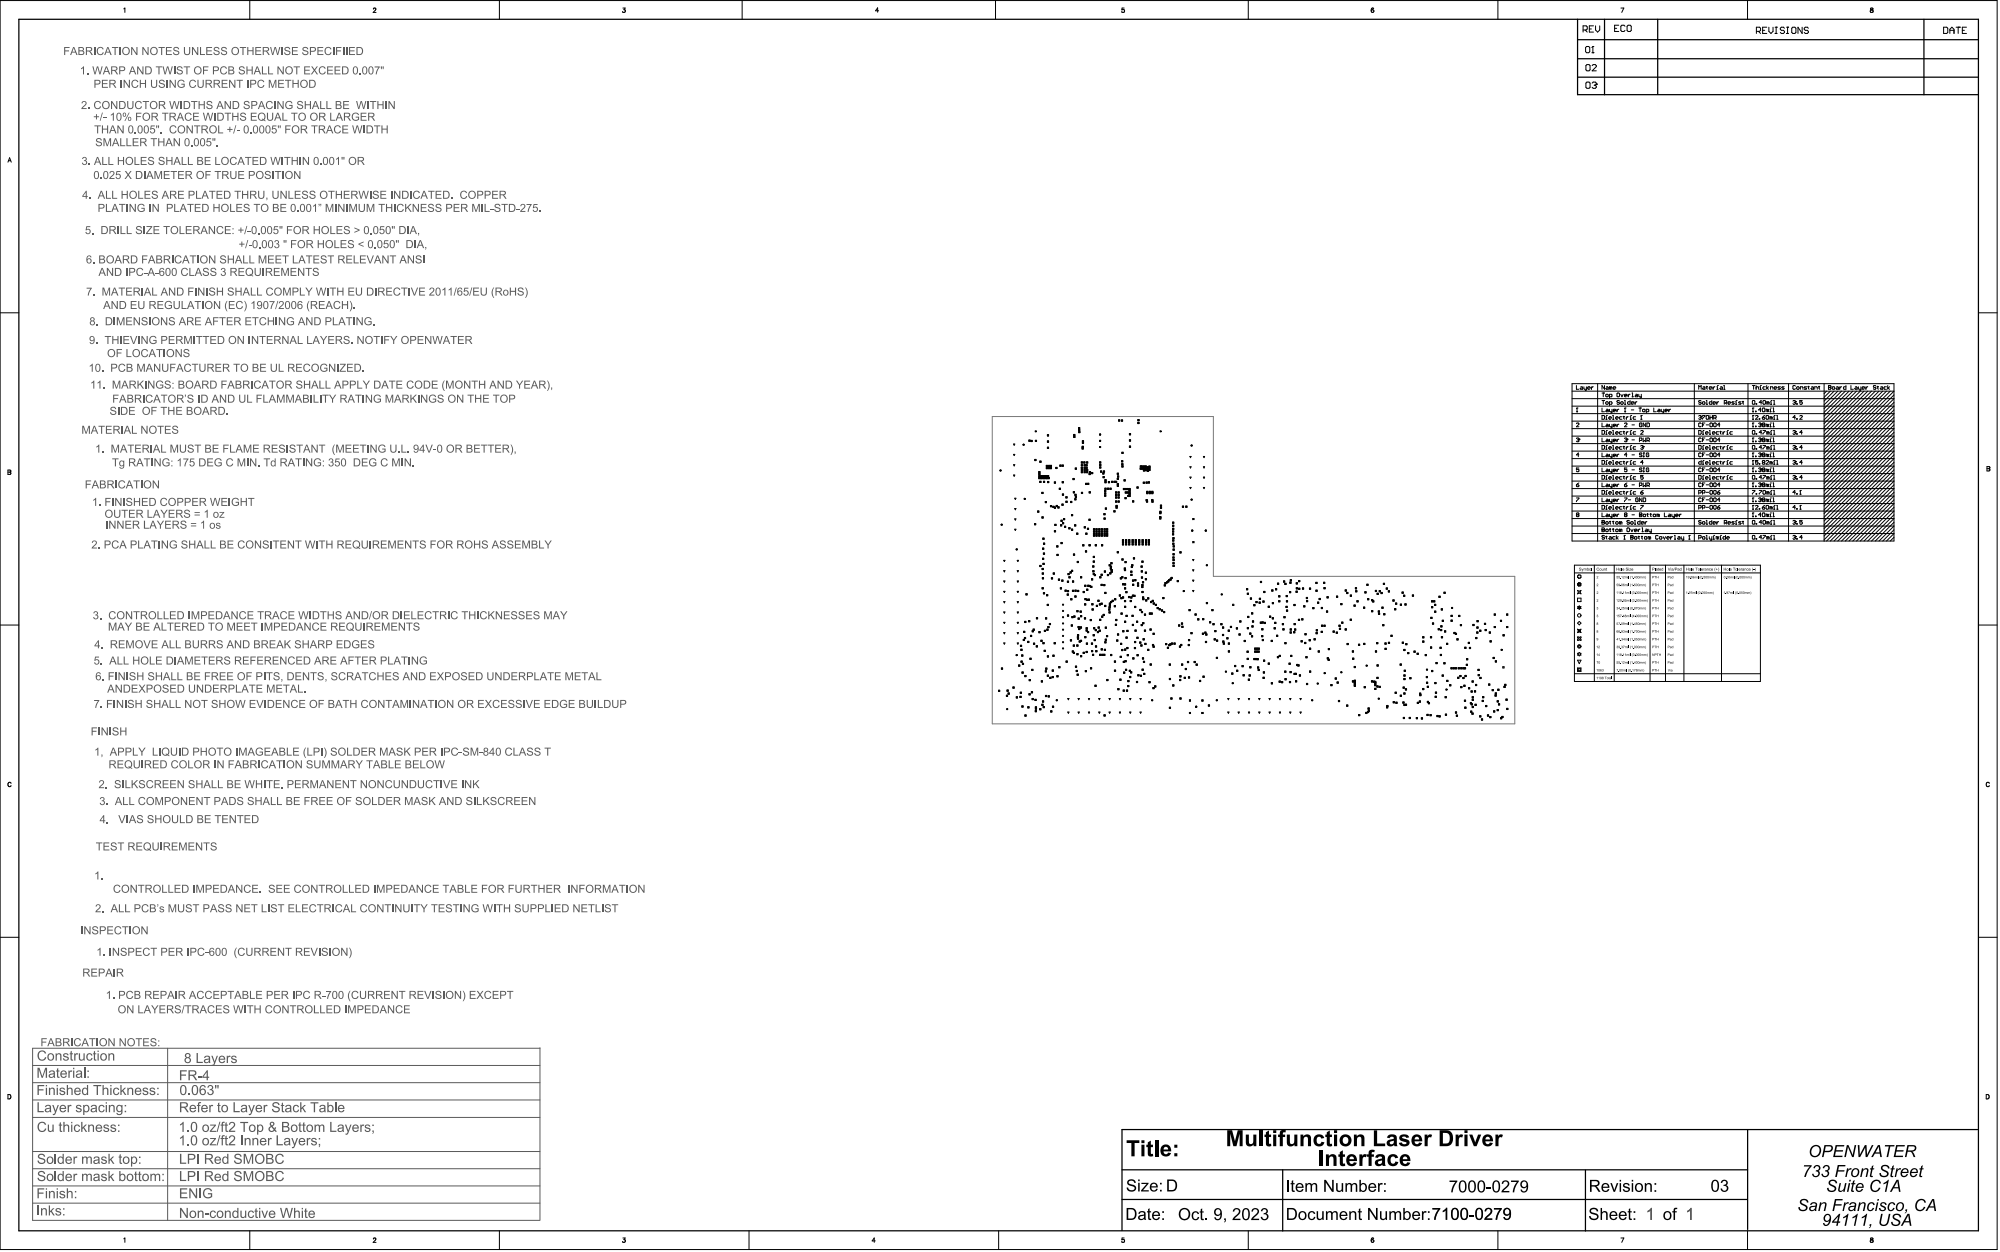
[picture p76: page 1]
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

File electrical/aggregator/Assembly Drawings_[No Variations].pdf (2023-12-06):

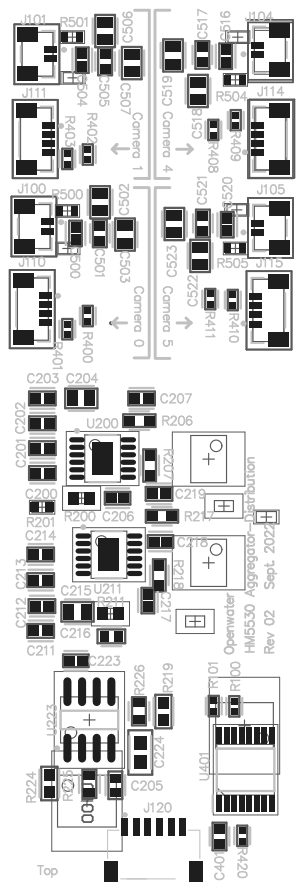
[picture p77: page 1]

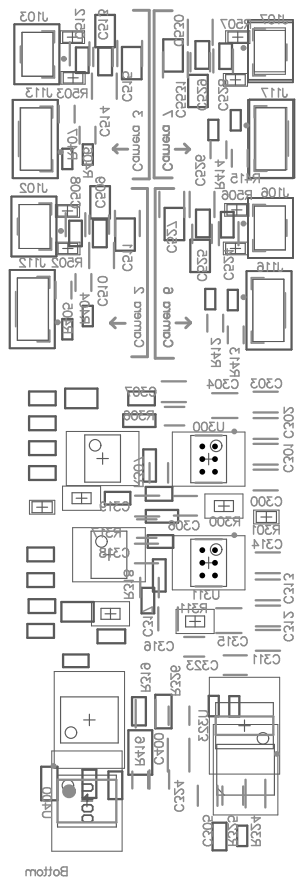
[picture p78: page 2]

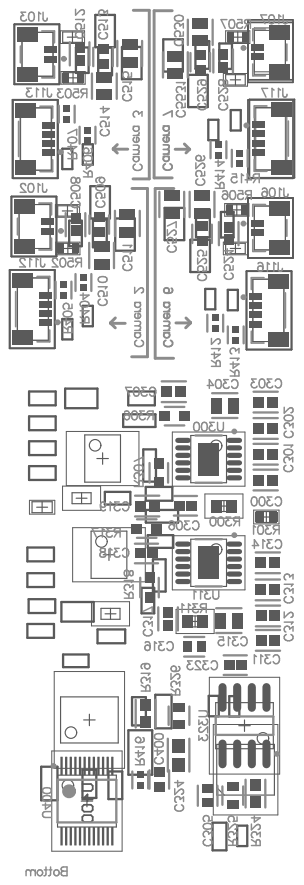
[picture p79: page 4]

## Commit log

2023-12-06 added large file
    [7000-0235 - VISOR ASSEMBLY, GEN 2.5 - R01.STL, 7000-0246.STEP]
2023-12-07 changed folder names
    [7000-0246.STEP, 7000-0272.STEP, BOM_[No Variations].csv, STEP_[No Variations] for 7000-0133 Rev 02-PCB, TA Mount2.PcbDoc.step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]
